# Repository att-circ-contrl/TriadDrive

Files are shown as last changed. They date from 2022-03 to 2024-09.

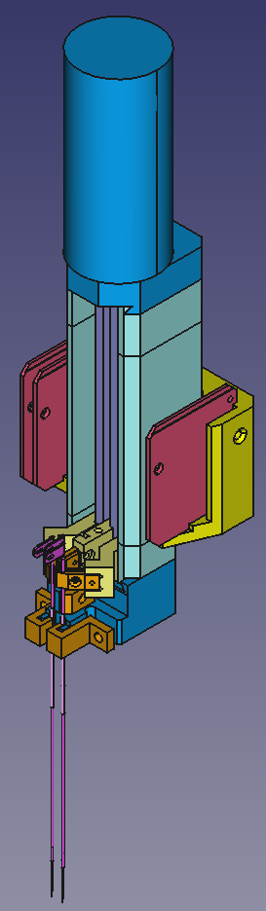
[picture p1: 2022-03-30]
drive-close-short/renders/20220329-nn-assembly-iso.png

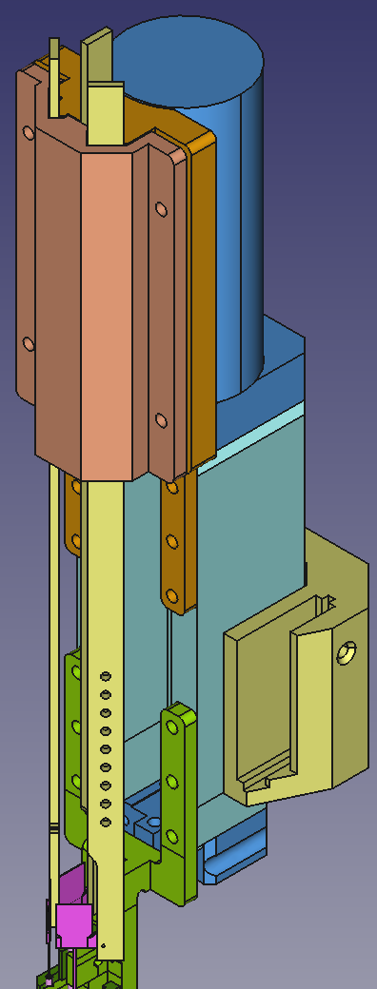
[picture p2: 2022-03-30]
drive-close-atlas/renders/20220317-rod-guide.png

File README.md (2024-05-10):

# Womelsdorf Lab Probe Drives

## Overview

This project covers the design of the probe drives used by the Womelsdorf
lab. As of 2022, these are mostly derivatives of the "Triad drive" 3-probe
drive commissioned in **FIXME - year** from Kevin Barker of Neuronitek.

The original "Triad" drive has three BNM07-1207 Namiki motors, each with a
105x reduction gear (SPG07-105). These drive #0-80 threaded rods, which move
probe-holding "arms" along paths defined by the outer shell of the drive
(the "body") and an internal "girder" with precisely-machined channels.

Derivative variants of the "Triad" drive replace the arms, the outer shell
of the drive, and the foot of the drive, but keep the basic architecture the
same and do not modify the motor section.

Alternate drive designs that are not direct derivatives of the "Triad" drive
are noted where present.

## Folders

Top-level folders:

* `aux-XXX` -- CAD files and notes specific to a given auxiliary tool.
* `drive-XXX` -- CAD files and notes specific to a given drive variant.
* `notes` -- Assorted notes that apply to several different devices.
* `obsolete` -- Devices and specifications that are no longer in service.
* `procedures` -- Assorted SOPs that apply to several different devices.
* `reference` -- Assorted reference material that isn't vendor documentation.
* `vendor-docs` -- Vendor-provided documentation and datasheets.
Under vendor copyright.

Sub-folders in `drive-XXX` and `aux-XXX`:

* `bom` -- List of vendor-supplied parts needed.
* `cad` -- Mechanical design CAD files. These are in FreeCAD format.
* `cad-ext` -- Mechanical design CAD or IGES files imported from a different
folder or provided by external sources (usually Isaac).
* `datasheets` -- Vendor-supplied mechanical drawings and component information.
* `drawings` -- Mechanical drawings of various components.
* `iges` -- Exported mechanical designs in IGES format.
* `meshes` -- Exported solid models in STL format.
* `notes` -- Assorted notes that are specific to this device.
* `photos` -- Photographs of the device or of associated equipment.
* `procedures` -- SOPs that are specific to this device.
* `renders` -- Screenshots of CAD views of various mechanical assemblies.

## Specific Designs

Active Triad drive variants are as follows:

* `drive-kevin` --
This is the initial Triad drive designed by Kevin for the Womelsdorf lab.
There were two variants: the "old" variant had a 45mm long channel for the
arms and the "new" variant had a 55mm long channel.

* `drive-close-short` -- This is a short-reach design with closely-spaced
probe sites. This drive is in service (with Kevin-style clips; the M0.5
screw-mount arms are obsolete). This can hold tungsten probes, NeuroNexus
probes, and Diagnostic BioChip probes (but not Atlas probes).

* `drive-close-long` -- This is a long-reach drive with the same
closely-spaced sites as the short-reach drive. This drive is in service.
Probes are held using Kevin-style clips. Guide tubes are held by a "foot"
that extends into the chamber. This drive is mainly used with Diagnostic
BioChip probes, which have a mechanical conflict between the probes and
guide tubes that limits range with the short-reach drives.

* `drive-close-atlas` -- This is a long-reach drive that is intended to hold
Atlas probes using the same "rectangular rod" scheme as the obsolete "v2b"
drive. This drive provides close-spaced probe sites with somewhat wider
spacing than the other close-spaced drives.

* `drive-kia-dev` -- Modified long-reach drives intended to work with
Diagnostic Bio-Chip probes, developed by one of our postdocs. This folder
contains his development tree (Autodesk CAD files, STL meshes, and gcode
for the printer he used).

Relevant auxiliary components are as follows:

* `aux-cabling` -- This folder contains documentation and models for
cables and connectors that the Triad drives and probes interface with.

* `aux-clips` -- This folder contains CAD models of clips used to hold
probes and guide tubes. Some are compatible with Kevin-style clip mounts,
while others are intended for different mounting methods.

* `aux-jig-atlas-long` -- This folder contains design files for tools for
loading Atlas probes into long-reach drives (drives that use the "rectangular
rod" system for holding probes).

* `aux-jig-nnex` -- This folder contains design files for the jig used to
pre-load NeuroNexus probes into guide tubes. The same jig works with
Diagnostic BioChip probes if the block holding the probe is shimmed with
tape to raise it.

* `aux-mounts-dbc` -- This folder contains cable mounts that replace the
mounting clip of the Triad drive. These hold the ZIF-clip connector boards
used with the 2022 Diagnostic BioChip probes.

* `aux-mounts-hflex` -- This folder contains cable mounts that replace the
mounting clip of the Triad drive. These hold the "heavy flex" analog signal
cables used with Atlas and NeuroNexus probes.

* `aux-probes` -- This folder contains CAD models of probes and CAD models
of printable components for making mechanical mock-ups of probes.

* `aux-proxies` -- This folder contains printable simplified proxy models
of drives and associated hardware. These are stencils intended to be used on
the mounting frame to check drive setups without needing to fully configure
drives.

* `aux-washers` -- This folder contains spacer "washers" used to raise the
Triad drives above their default mounting locations.

Drives not directly tied to the Triad Drive design:

* `drive-compact` -- This is a single-probe miniature manual drive intended
to be arrayed inside the chamber. This is a more manufacturable variant of
the 2018 "semi-chronic" drive concept.

* `drive-unidrive` -- This is a proof-of-concept single-probe drive based
on the same principles as the Triad drive but designed to be easier to
manufacture.

## Remarks

* I've been repeatedly reassured that the Womelsdorf Lab owns all of the IP
for the original drives that we commissioned, so there should be no IP issues
with derived variants.

* Kevin is a superb engineer. Every aspect of his original design is there
for a reason, and the reasons are not always obvious. Kevin also gets
precision about twice as good as standard "shop" precision (better than
0.1mm, vs typical shop precision of 0.15 mm or worse). The downside to this
is that understanding the original design was nontrivial and third-party
parts typically have wobble due to worse tolerances.

* I have a love/hate relationship with the `FreeCAD` program. It works
_just_ well enough that it isn't worth my time to learn a new program, but
it has strange ideas about how many operations should be done and it
lacks several features that would be helpful for building and testing
models. If you need to modify existing mechanical models, I suggest
importing `.iges` models into your preferred CAD program.

* IGES models should be saved as solids (type 186), rather than as surfaces
(type 144). Surfaces are the default, but solids can have additional
operations performed on them after import (especially boolean operations).

_This is the end of the file._

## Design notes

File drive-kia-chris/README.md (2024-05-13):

# Chris's Copy of Kia's Long-Reach Drive

## Overview

The close-spaced long-reach drive was modified by one of our postdocs
(Kia) to work more effectively with his setup. This is my annotated copy
of the parts that were put into service.

NOTE - In the future I may CAD up my own versions of these, optionally with
modifications. For now, it's just a handy way of determining which parts
were actually used out of the many variants in Kia's dev tree.

Salient changes that Kia made:

* Drive components were mostly compatible with filament-printing (he used
that for prototyping).

* Drive feet were modified to be as flat as possible, for optimum access
to sites near the side of the chamber.

* Kia used captive nuts and epoxied-in-place nuts in lieu of hand-threading
holes. This solved the durability problem with holes that were threaded in
plastic.

## Notes

Unsorted notes:

* The mockup shows the drive foot reaching into the chamber, but the other
way of using these is to use stand-offs on the mounting post to raise the
drive so that the drive foot is above the chamber. This gives access to
sites next to the chamber wall without having to have the drive reach across
the entire chamber. The mounting frame photograph illustrates this
configuration.

* There are many incremental variants of the STL files. The best way to tell
which ones are the final ones is to look at the datestamps (in the
`zz-datestamps` folder in the `drive-kia-dev` folder).

* Kia's STL files and my IGES files all have varying coordinates between
parts. I've arranged everything in the mockup and re-exported it to the
`exported` folder to try to get everything into a consistent coordinate
frame.

_This is the end of the file._

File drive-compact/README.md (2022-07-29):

# Miniature Single-Probe Drive

## Overview

This is a proof-of-concept design for a manual drive that uses the same
principles as the 2018 "semi-chronic" paperclip-sized drive, but with parts
that are easier to make and to assemble.

These are driven using a hex-drive screw that's coupled to the drive rod.
The intention is that a motorized hex driver could be placed above the drive
to allow computer-controlled driving. Hex-drive is also far less slip-prone
than flat-bladed driving for manual drive, and doesn't require pressure like
Phillips does.

## Notes

* Natural widths from assembly screw lengths are 2.4mm (3/32"), 3.2mm (1/8"),
and 4.8mm (3/16").

* Another width constraint is side wall thickness for the drive screw and
alignment pins. The drive screws are 1.5mm wide (#0-80) and the bushing tubes
around the alignment pins are 2.1mm (14ga) or 2.4mm (13ga) wide, for 1/16"
pins.

* Minimum collar width is 4mm, with D-profile shafts and 1/16" set screws.
For anything narrower, the drive shaft and drive screw will have to be
brazed or welded together inside a coupling tube.

* Natural height of the alignment pin holding frame is 1/4" (6.35mm).
Useful minimum is 5mm. Natural depth of the bottom is about 15mm (much more
and it starts conflicting with tissue, depending on location).

* Drive rod length is 1", 1-1/2", or 2", from McMaster-Carr.

* Drive screw length for socket-head is 1/2" if 316, or up to 1-1/2" 18-8.

_This is the end of the file._

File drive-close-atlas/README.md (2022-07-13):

# Close-Spaced Drive for Atlas Probes

## Overview

This folder contains a variant of the long-reach "v2b" drive that has
close-spaced sites. This drive is intended for use with flanged Atlas probes.

The probes are mounted on rectangular "rods" that are in turn moved by
modified arms. A guide block keeps the "rods" in alignment. A "fork" extends
down into the chamber, and guide tubes are mounted to the fork. The body and
rods are identical to the "v2b" version. The guide block, arms, and fork are
new.

**NOTE** - The "Atlas" drive uses the "Atlas" sites in the site diagram
(2.0mm spacing), which differs from the more closely spaced sites used with
DBC and NeuroNexus probes (1.0mm/1.5mm spacing). Distance from the mounting
post also differs.

A variant of this drive uses clip-based arms instead of rods, omitting the
rods and upper guide block. This is intended to work with tungsten probes
using the same guide tube pattern as Atlas probes.

## Atlas Notes

* The Atlas probe cables have to bend around backwards to reach the cable
mount. This is because the original Atlas use-case had heavy flex and the
drive on opposite sides of the chamber, whereas the Triad drives have
heavy flex mounted on the drives.

* Mounting the Atlas probes is non-trivial, because they break if you look
at them funny and the thin-flex connected to them isn't much stronger.

* With a plastic foot, *the side guide tube mounts deflect*, pinching off
the middle channel and moving each guide tube inwards by about 0.4mm. The
probe mounts have enough compliance to tolerate this, but it's very much
not an ideal situation.

## Clearance and 3D Printing Notes

* Arms need to be made with tolerances better than standard shop and
printing tolerances. Otherwise the clearances needed for reliable assembly
are large enough that the arms wobble. We can't actually get arms made
with the required precision, so instead several versions of the arms are
made with nominal thicknesses varying in steps of 0.05 mm. In any given
batch, one version of any given arm should be the right thickness.

* Arms with tight clearances should be oriented with their long axes in the
Z direction for 3d printing. This gives 0.05 mm tolerances on the other axes
when using Proto Labs' "micro-resolution" printing process.

* As of June 2022, the "thick" variants of the arms work best in the drives.

_This is the end of the file._

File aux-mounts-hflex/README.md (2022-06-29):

# Cable Mounts for Heavy Flex

## Overview

These folders contain models and drawings of cable mounts intended to hold
the "card" ends of the "heavy flex" cables, securing the ends of the cables
to the Triad drives.

The cable mounts replace the mounting clip on the Triad drive (holding the
drive to its mounting post).

## Notes

* The single-slot sides anchor the heavy flex cables using a 5/16" #0-80
flat-head screw. The two-slot sides use a 3/8" #0-80 flat-head screw.

* Be careful installing the screws. There's only about 2mm of threaded
area, and it's easily stripped.

_This is the end of the file._

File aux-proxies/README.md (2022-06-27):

# Mechanical Proxies

## Overview

This folder contains models of mechanical proxies of each of the drive
variants in service. These are used for planning the configuration of the
drives; proxies are mounted on a mockup chamber and adjusted to have guide
tubes in the desired locations.

(The original proxy for the stock tungsten drives was made by Brainsight
in the 2010s, I think. The new proxies are intended to be 3d printed.)

The proxies have optional obstruction templates that may be attached. Without
the templates, the goal is to show where the guide tubes will be positioned
with maximum visibility. With the templates, the goal is to see whether nearby
drives will conflict with each other.

## Specific Models

Drive proxies (representing the drive bodies and guide tubes):

* `drive-close-atlas` -- This represents the close-spaced drive for Atlas
probes with guide tube mounts inside the chamber, using the 2.0/2.0/1.5 mm
hole pattern.

* `drive-close-long` -- This represents the "close-spaced long-reach"
drive for NN and DBC probes with guide tube mounts inside the chamber, using
the 1.0/1.5/1.5 mm hole pattern.

* `drive-close-short` -- This represents the "close-spaced short-reach"
drive with guide tube mounts above the chamber, using the 1.0/1.5/1.5 mm
hole pattern.

* `drive-stock` -- This represents the stock "kevin" drive with a bundle
of three guide tubes in contact with each other.

Cable mount proxies (representing mounts for either the "heavy flex"
cables or the Diagnostic BioChip adapter boards):

* `dbc-zif-narrow` -- This represents a Diagnostic BioChip board mount plus
attached ZIF-clips, intended for narrow-body (stock) drives.

* `hflex-narrow` -- This represents a "heavy flex" mount intended for
narrow-body (stock) drives.

* `hflex-wide` -- This represents a "heavy flex" mount intended for
wide-body (Atlas) drives.

Obstruction templates (representing space taken up by drive arms and by
guide tube mounts):

* `close-atlas` -- This represents a standard (two-level) foot used with
the Atlas probe long-reach drives.

* `close-short-1pc` -- This represents a low-profile foot for the
"close-spaced short-reach" drive that uses a single clip to hold all three
guide tubes.

* `close-short-2lv` -- This represents a standard (two-level) foot for the
"close-spaced short-reach" drive that uses one clip for each guide tube.
This is also used for the "close-spaced long-reach" drive.

* `close-short-3pc` -- This represents a low-profile foot for the
"close-spaced short-reach" drive that uses one clip for each guide tube.

_This is the end of the file._

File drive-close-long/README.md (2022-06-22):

# Close-Spaced Long-Reach Drive

## Overview

This folder contains a long-reach variant of the close-spaced short-reach
drive, intended for use with Diagnostic BioChip probes. This eliminates
mechanical conflicts between the probe and guide tube, allowing the full
range of drive travel to be used (so that the probes can reach as far as
possible into tissue).

For this variant, the drive "foot" is extended to incorporate a
downward-projecting shaft similar to that of the "forks" used in
"v2b"-derived drives. This results in geometry that is difficult to machine,
but 3d printed versions should work (the shaft is 3mm thick to ensure
sufficient strength and rigidity).

Guide tubes are in the same locations as with the close-spaced short-reach
drives, so the stock (narrow) body and short-reach drive's arms are used.

## Clearance and 3D Printing Notes

* Arms need to be made with tolerances better than standard shop and
printing tolerances. Otherwise the clearances needed for reliable assembly
are large enough that the arms wobble. We can't actually get arms made
with the required precision, so instead several versions of the arms are
made with nominal thicknesses varying in steps of 0.05 mm. In any given
batch, one version of any given arm should be the right thickness.

* Arms with tight clearances should be oriented with their long axes in the
Z direction for 3d printing. This gives 0.05 mm tolerances on the other axes
when using Proto Labs' "micro-resolution" printing process.

* As of June 2022, the "wide" variants of the arms work best in the drives.

_This is the end of the file._

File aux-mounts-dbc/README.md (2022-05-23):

# Board Mounts for Diagnostic BioChips Probes

## Overview

These folders contain models and drawings of board mounts intended to hold
the boards and ZIF-clips used with Diagnostic BioChips probes. The boards
screw into the mounts and the ZIF-clips clip on to the boards.

The board mounts replace the mounting clip on the Triad drive (holding the
drive to its mounting post).

## Notes

* These are intended to be 3d printed in a rigid plastic. Nylon and printed
polypropylene flex too much at the mounting posts.

* The new versions of these mounts attach Kevin-style. The two faces on
each side of the post aren't flush with each other. One mates with the
drive, leaving a small amount of clearance in the post channel. The the
other has clearance, allowing the clamp to bend as the screw is tightened
until the post and channel fully engage with each other.

* There are multiple versions of the mounts, with different post channel
widths. Choose the version that has the least clearance around the post.
Different versions are identified by different markings.

_This is the end of the file._

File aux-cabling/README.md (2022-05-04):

# Cables and Connectors

## Overview

This folder contains drawings and models for some of the cables and
connectors used with the Triad drives and probes.

This is not a complete list or a complete specification; those are beyond
the scope of this project. The intent is to provide enough information to
allow compatible cable mounts and cabling arrangements to be designed.

## Specific Cables and Connectors

* We use custom headstages built into 128-channel TDT ZIF-clips. A rough
model of a ZC128 clip is provided.

* The "heavy flex" cables are used to connect Atlas and NeuroNexus probes to
ZIF clips (and to provide strain relief). In both cases, the probe is
connected to the heavy flex via a much smaller "thin flex" cable.

## CAD Files

* The "`atlas-flex-2020.fcstd`" CAD file contains a model of the thin-flex
Atlas cable, and an assembly of these cables with the "carrier card" from
the heavy-flex cable. The "carrier card" model is reconstructed from a mesh,
rather than from the original solid model.

_This is the end of the file._

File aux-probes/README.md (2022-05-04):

# Probe Models

## Overview

This folder contains drawings and models for the probes used with the
Triad drives.

This is not a complete specification; that's beyond the scope of this
project. The intent is to provide enough information to allow the design of
drives that are mechanically compatible with the probes.

## Specific Probes

* Atlas probes were ordered in 2017.

These were originally intended to be used with a dense-packed semi-chronic
drive, which secured the probes and guide tubes to the drive with flanges
and tiny screws. With the Triad drive we can use different guide tubes and
clamp them normally, but the probes will have to be secured with screws (the
flanges are permanently bonded and the probe shanks are too fragile to
reliably grab).

The Atlas probes have "thin flex" ribbons that connect to our "heavy flex"
cables. The Atlas probes are permanently bonded to the heavy flex.

* NeuroNexus probes were ordered in 2018 and 2021.

They were ordered with flanges for compatibility with the Atlas drive
hardware, but in practice are secured using clips. The shanks are stainless
steel tubes, making them much easier to secure and to handle.

The NeuroNexus probes have hair-thin flex cables which are bonded to tabs
that connect to our "heavy flex" cables. These may be connected and
disconnected from the heavy flex as-desired.

* Diagnostic BioChip probes were ordered in 2022.

These do not have flanges, but instead have a 5mm collar of hypodermic
tubing for handling.

The DBC probes do not connect to "heavy flex". Instead, they have their own
ZIF-clip compatible adapter cards, which are connected to the probes using
a short length of delicate thin flex. The adapter cards need to be mounted
close to the probes and the ZIF-clips need to connect directly to the adapter
cards.

## CAD File Notes

* The presently active CAD file is "`probe-models-2022.fcstd`".

* The 2020 CAD file contains old models for NeuroNexus probes. The "sleeve"
version was an alternate implementation that wasn't made; it can be ignored.
The file has copies of the old Atlas models, but these were reconstructed
from meshes instead of from the original solid models.

_This is the end of the file._

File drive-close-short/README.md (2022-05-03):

# Close-Spaced Short-Reach Drive

## Overview

This is a modification of the "stock" Triad drive that replaces the foot
and the arms (in the same manner as the "v2c" variant did). It keeps the
original "narrow" body.

"Silicon" arms with holes to screw in flanged probes were made, but were a
pain to use, and it turned out that NeuroNexus probes can be held by the
clips Kevin provided to us (albeit at risk of metal fatigue). So, only the
"tungsten" arms are needed with this design.

This design can work with tungsten, NeuroNexus, and Diagnostic BioChip
probes, with appropriate cable holders.

## Variants

The following variants are in service:

* The "stacked" foot is the original version, with the middle guide tube
clip raised above the side clips. The central guide tube is held with a
flat "6p5" clip and the side guide tubes are held with "J-clip" clips.

* The "1pc" low-profile foot uses a single clamp to hold all three guide
tubes. It's difficult to individually adjust guide tubes with this drive,
and removing any guide tube requires removing the clamp.

* The "3pc" low-profile foot uses three clamps to hold the guide tubes, with
the middle clamp screwing into the side clamps rather than into the base of
the drive. In principle the guide tubes can be individually adjusted with
this setup (though adjusting any screw alters pressure on all three clamps).
Removing either of the side guide tubes requires first removing the middle
clamp.

## Notes

* The IGES files for the foot and J-clip are surfaces, not solids.
* I think Isaac's exported arms are solids but I'm not certain.
* The original version (from 2021-11-04, with Z-clips) didn't work; the
clips would slide off of the guide tubes. The J-clips fixed this (from
2021-11-18).
* The "`triad-arms-ref-202203`" CAD file imported Isaac's arms for purposes
of making mechanical drawings. These are not authoritative but are a good
starting point. The DBC arms are the current version.
* FIXME - As of 2022-04-21, I'm not sure either the 1pc or 3pc clamps will
work (untested). The 1pc one might have difficulty grabbing the middle tube
due to bowing, and the 3pc one may have difficulty grabbing the side tubes
when the middle clamp is tightened and/or difficulty installing the middle
clamp when the side clamps are tightened.

_This is the end of the file._

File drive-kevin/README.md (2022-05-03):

# Stock ("Kevin") Triad Drive

## Overview

This folder documents the "stock" version of the Triad drive. These were
produced by Kevin Barker of Neuronitek on a contract for Thilo's lab.

## Notes

* Most parts were made by machining, but some parts were made by EDM by a
third-party vendor (I'm not sure who Kevin used for this).

* Kevin miniaturized the drives as much as possible (at Thilo's request).
Consequences of this include additional complexity, thin walls near several
holes, and the need for extremely close tolerances.

* Kevin got part fits with tolerances about twice as good as any other
vendor I'm aware of (about 0.05 mm as far as I can tell). He did this by
a combination fo careful setup and by hand-modifying individual sets of
mating parts.

The practical upshot of this is that any parts we get made for the Triad
drives will be a bit loose, due to the fact that we can't precisely match
the fit with the existing parts.

* The models in the "`iges`" folder should be considered authoritative.
These are my best guess as to the geometry of the actual parts. NOTE - These
were exported as surfaces rather than solids, so there may be issues
importing them.

* There are two types of meshes in the "`stl`" folder. Ones with the "`-sw`"
suffix have been modified to be compatible with Shapeways' 3d printing
design rules (mostly avoiding sharp concave edges and thin walls). Ones
without the "`-sw`" suffix were exported from the original models as-is.

## Variants

* The "old" variants have 45mm bodies made from black Delrin. The "new"
variants have 55mm bodies made from white Delrin. The "new" variants are
labelled "rev 3".

* The guide tube clip geometry is different for "old" and "new" variants.
The foot's mounting for the guide tube clip is also different.

* At least one variant exists that mounts five or six probes and guide
tubes (two per arm). If I understand correctly these were used for SPME
experiments.

_This is the end of the file._

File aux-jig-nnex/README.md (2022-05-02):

# Hand-Loading Jig for NeuroNexus Probes

## Overview

This folder contains drawings and models for a jig used to load NeuroNexus
probes into guide tubes.

**NOTE** - This is presently also used to load Diagnostic BioChip probes
into guide tubes, but the probe holding part needs to be shimmed on the
bottom with masking tape in order to have the correct alignment.

## Using the Jig

To use the jig:
* Clamp the guide tube on to the right (moving) block. Move it a safe
distance away.
* Place the probe on the left (fixed) block. The green tab on the NeuroNexus
probes can be placed to stand up in one of the grooves in the rubber
portion; for DBC probes, just rest the card on the rubber.
* Holding the probe in place with a fingertip, clamp it down.
* Put the surgical loupe on. You're going to have to align the probe tip and
guide tube by eye.
* Move the guide tube closer to the probe. When the probe tip and the
entrance to the guide tube are near each other, ensure that they are aligned
by applying gentle pressure to the mounting blocks (they can deform slightly),
and/or by applying gentle pressure to the clamp holding the probe (the probe
will bow slightly, adjusting its height).
* When the probe and guide tube are aligned, bring them together.
* When the probe is fully inserted, hold the probe and guide tube in place
with a fingertip and un-clamp both.
* Remove the probe and guide tube by holding the guide tube with forceps,
keeping it tilted up so that gravity moves the probe into the tube instead
of out of the tube. Hold the green tab (NN) or circuit board (DBC) with
forceps to prevent it from pulling on the thin flex.

## Miscellaneous Notes

* Some or all of the IGES models will have been exported as surfaces rather
than solids.

_This is the end of the file._

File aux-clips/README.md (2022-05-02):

# Clips for Probes and Guide Tubes

## Overview

This folder contains drawings and models for some of the clips used to hold
probes and to hold guide tubes with the Triad drives.

This is not a complete list, but should cover the types that are presently
in service. Historically two other attachment methods were also used (using
screws and flanges to mount individual probes and guide tubes, and using
a larger clamp to hold multiple guide tubes at once), but clips were the
most practical system.

The guiding principles are as follows:

* It should be possible to remove individual probes and guide tubes without
disturbing the others.

* It should be possible to position probe sites close to each other (2mm or
closer).

* Nobody should have to reinstall M1 screws or do anything with M0.5
screws in order to add or remove probes or guide tubes. #0 screws are
preferred over M1 where practical.

Several fabrication methods are available:

* 3D printing was used for large clamps and is still used for the assemblies
that clips screw on to. Printed plastic parts are too weak to use for the
clips themselves and printed metal parts have resolution too poor to use,
with rare exceptions.

* CNC machining is used where practical, but has strong constraints on
geometry (in particular thickness).

* EDM is used for making thin clips with high precision out of stainless
steel, but finding vendors for this is a pain and turnaround time is long.

## Specific Clips

* The "Kevin" clips were made by EDM and were intended to hold 200 micron
tungsten probes. In practice they'll hold 125 micron probes that are
shimmed with tape, and they've been used to hold 400 micron NeuroNexus
probes (although this will eventually cause metal fatigue). These use M1
screws for mounting and for closing.

* The "6p5" straight clips are made out of CNC machined PEEK. These use #0
screws for mounting and closing and are somewhat bulkier than Kevin clips.

* The "j-clip" clips are made from 3d printed resin (Proto Labs' "ABS-like
micro-resolution" process). These are used as guide tube clamps with
certain close-spaced probe layouts. The geometry and tolerances made 3d
printing the only option. So far they've held up in use.

* The "compat-630" EDM clips are very similar to the Kevin clips and are
intended to hold 630 micron guide tubes and probe collars.

* The "cnc-630" clips were intended to hold 630 micron guide tubes and
probe collars and to be made using Proto Labs' CNC service.
**Obsolete** - They ended up being too bulky and Proto Labs wouldn't
machine the probe registration notches.

* The "3dp-630" clips were intended to hold 630 micron guide tubes and
probe collars and to be made using Proto Labs' stainless steel 3d printing
service. **NOTE** - These are very difficult to hand-tap.

_This is the end of the file._

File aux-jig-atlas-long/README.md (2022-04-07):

# Atlas Probe-Loading Tools for Long-Reach Drives

## Overview

This is a jig and a set of manipulation tools intended for attaching Atlas
probes to the "rectangular rods" used by long-reach drives, and for mounting
the probe-and-rod units into those drives.

## Notes

* The probe needs to be held by its flange, using a padded clamp. If the
flex cable is held instead, the probe bounces around and is very difficult
to control. Attempting to hold the shank will break the probe (they break if
you look at them funny).

* After the two parts are attached, the clamp has to hold the probe to the
rod semi-rigidly to prevent forces on the cable from moving the probe, but
needs to have enough compliance to allow the probe tip to be manually aimed
at the guide tube.

* As with any Atlas probe setup, the M0.5 screw holding the probe needs to
be backed off half a turn so that the probe can move enough to self-align
with the guide tube.

_This is the end of the file._

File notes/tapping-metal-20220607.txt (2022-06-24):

Notes for tapping M1 threads in 3d printed steel clips:

- As soon as there's _any_ resistance (about half a turn of cutting), back
  off half a turn to a full turn.
- If there's still resistance when resuming after that, back all the way
  out and clear chps with canned air.

This was for relatively shallow holes (1mm deep).

This should work for brass, aluminum, and 3d printed 316 steel. It may not
work with hard steel (heat-treated printed 17PH, machined steel parts, etc).

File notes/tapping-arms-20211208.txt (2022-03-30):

To tap 3d printed plastic arms without damage:

- Use the 3/64" (#0 tap) drill to widen the holes.
- Start tapping. As soon as there's resistance, _stop_ and back out.
- Use canned air to clean the tap and clear the hole.
- Resume tapping. As soon as there's resistance, _stop_ and back out.
- Repeat the above steps until the hole is fully tapped.
- Clean the tap and clear the hole, and then run the tap through the hole
  again for a finishing pass.
- Clean the tap and clear the hole, and use a #0-80 screw to test the hole.
  The screw should engage easily with no resistance at any point.

Tapping too aggressively does the following:

- The side-walls bulge out. Best-case they'll need to be filed down, and
  in the worst case they'll break (prints are weak and walls are thin).
- The side-walls will apply pressure, squeezing the screw. This will cause
  the arm to get stuck on the drive screw.

.. The procedure outlined above will eliminate these problems.

It's a good idea to use a similar procedure with harder materials, too. It's
also important to back out and break chips when working with, e.g., PEEK.

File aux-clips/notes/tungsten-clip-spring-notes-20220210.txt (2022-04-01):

Microscope measurements gave:

- Spring is 0.25 mm thick.
- Clearance between flats was 0.05 mm.

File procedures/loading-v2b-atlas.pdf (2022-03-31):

Loading Atlas Probes Into the v2b Triad Drives Christopher Thomas - 2020 July 17

FIXME - Add photos

1. Remove the cable shelf assembly and Triad mounting post from the “first and second probe” base plate.
2. Insert the Triad drive on to the mounting post, install the mounting post on to the base plate, and then reinstall the cable shelf assembly on the base plate.
3. Move the Triad arms to their topmost positions.
4. Install the “first” cannula jig, using shims to adjust the height. Verify positioning with a loupe.
5. Install the “first” probe jig. The probe jig should start flush-right in its well, to give it space to move left. Install the thin flex clip screw, but not the clip itself, in the probe jig.
6. Move the middle Triad arm down to register with the probe jig. Verify that the arm is seated on the jig shelf. Adjust this by changing shims.
7. Open the heavy flex clip. Holding the probe assembly’s thin flex using forceps and the heavy flex using your hand, position the probe near its loading position. Keep the probe above and slightly away from the Triad drive so that no probe contact occurs. Close the heavy flex clip to secure the heavy flex.
8. Transfer the forceps to your dominant hand, and place the probe across the probe jig with its tip over the cannula jig, adjusting it to its loading position. Install the thin flex clip by placing it, pressing down on it by hand, and tightening its screw with your other hand.
9. Visually inspect the probe shuttle using the loupe, verifying that it overlaps the mounting hole. Make small adjustments to the shuttle’s position if necessary by slightly loosening the thin flex retaining clip and moving the thin flex gently.
10. Rotate the entire mounting assembly so that you can see the shuttle and its mounting hole and easily access both of these with fine-point forceps.
11. Hold a M0.5 screw in the forceps with your non-dominant hand. Position its tip in the mounting hole and turn it two full turns using a miniature screwdriver in your dominant hand. The idea is to have it engage with the threads so that you can let go with the forceps.
12. Use your fingertips or fingernails on your non-dominant hand to stabilize the screwdriver tip while fully driving the screw. After reaching the screw’s limiting position, back it off by half a turn to allow the probe shuttle to slide and pivot.
13. Undo and remove the thin flex retaining clip. Also remove the screw that held the retaining clip.
14. Pressing the probe mounting jig towards the Triad drive, remove the mounting jig screw. Remove the probe jig shims, allowing the jig to drop while continuing to press it towards the drive (so that it does not contact any part of the probe). When the jig has dropped, remove it.

15. Align the probe with the registration surfaces on the cannula jig by applying gentle pressure to the thin flex, shuttle, and if necessary upper part of the probe shank. Use the loupe to verify that the probe is registered with the cannula.
16. Advance the probe tip into the cannula. Hand-feed the heavy flex cable through the (closed) heavy flex clip as necessary during this process. The desired stopping point is before the thin flex of the middle probe would interfere with loading the next probe.
17. Press the cannula jig towards the Triad drive, and remove it in the same manner as with the previous jig.
18. Seat the “second” cannula jig and “second” probe jig in the same manner as the first, with the second cannula jig aligned with the cannula and the second probe jig flush right..
19. Advance the upper arm of the Triad drive until it contacts the second probe jig. This arm should be to the left of the first probe’s thin flex, ensuring no mechanical conflict between the two flex cables after loading.
20. Position the second probe in its probe jig in the same manner as with the first probe (holding it by the thin flex near the probe, securing the heavy flex, manipulating the probe into position using the thin flex, and then securing the shuttle and thin flex). NOTE
- The position of the arms should result in the second probe’s tip being in a safe position over the cannula jig. If this is not the case, adjust the positions of the two arms until the probe may be safely positioned.
21. Install the second probe’s mounting screw in the same manner as with the first probe (rotating the jig assembly to a convenient position, holding the screw during the first two turns using forceps, advancing the screw fully, then backing off half a turn).
22. Remove the thin flex retaining clip and its screw from the probe jig.
23. Press the second probe jig towards the Triad drive, and remove it in the same manner as the first probe jig. Take care that it doesn’t apply undue force to the first probe’s thin flex when it drops (a small amount of contact can be tolerated). If necessary, remove shims one at a time to drop the jig in a controlled manner.
24. Register the second probe with the second cannula jig, using a loupe to verify that it will cleanly enter its cannula.
25. Advance the second probe into the cannula, stopping when its arm is aligned with the arm holding the first probe. Feed the second probe’s heavy flex through the (closed) heavy flex clip as necessary, taking care not to unduly perturb the first probe’s heavy flex.
26. Advance both probes into their respective cannulae, feeding both heavy flex cables as necessary. Stop when the tips of both probes become visible, and withdraw the probes 2mm past the point where the tips are no longer visible (to protect them from damage).
27. Install the heavy flex cables in their slots in the cable mount, advancing the heavy flex cables through their retaining clip as needed. When the cables have been screwed into their mount, the heavy flex clip may be opened.
28. Unscrew and remove the heavy flex clip assembly. Unscrew the Triad mounting post, and pick up the Triad drive (with mounting post). Loosen the clip mounting screws slightly, and remove the mourning post from the Triad drive.

29. Remove the heavy flex clip assembly and mounting post from the “third probe” base plate. Install the Triad drive on the mounting post, install the mounting post on the “third probe” base plate, and then install the heavy flex clip assembly on the “third probe” base plate.
30. Install the “third” cannula jig and the “third” probe jig as with previous probes. The probe jig should start off flush left.
31. Advance the last arm until it contacts the probe jig. Adjust shims for the probe jig ase in previous steps.
32. Position the third probe using the same method as with previous probes (holding it by the thin flex just above the probe, securing the heavy flex, adjusting position, and securing the shuttle and thin flex).
33. Install the third probe’s mounting screw in the same manner as with previous probes (making sure to back it off half a turn to allow movement).
34. Remove the thin flex clip and its screw from the probe jig. Press the probe jig towards the Triad drive, and remove it in the same manner as with the second probe jig (removing thin shims to drop it in a controlled manner).
35. Align the third probe with its cannula in the same manner as with previous probes. Advance it into the cannula, feeding the heavy flex through its clip as needed. The desired stopping point is at least 4mm into the cannula, so that lateral forces will cause the shank rather than the probe tip to touch the side of the cannula.
36. Press the cannula jig towards the Triad drive, and remove it in the same manner as the second cannula jig (removing thin shims to drop it in a controlled manner).
37. Advance the third probe until its tip is visible, feeding the heavy flex cable as needed. Withdraw the third probe 2mm past the point where its tip ceases to be visible.
38. Install the third probe’s heavy flex in the cable mount.
39. Un-clip the heavy flex, remove the heavy flex assembly, unscrew the Triad mounting post from the base plate, pick up the Triad drive, and remove the Triad mounting post from the Triad drive. The drive is now loaded.

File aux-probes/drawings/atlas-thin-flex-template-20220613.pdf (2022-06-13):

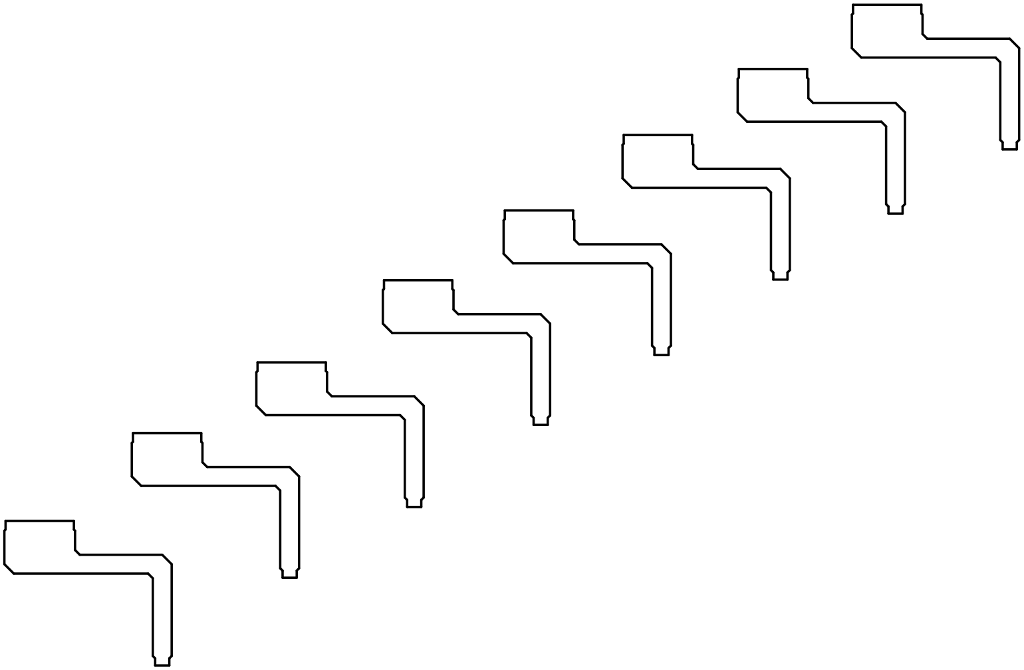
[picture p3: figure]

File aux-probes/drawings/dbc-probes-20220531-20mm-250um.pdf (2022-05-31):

# Diagnostic BioChip Probes

## 31 May 2022

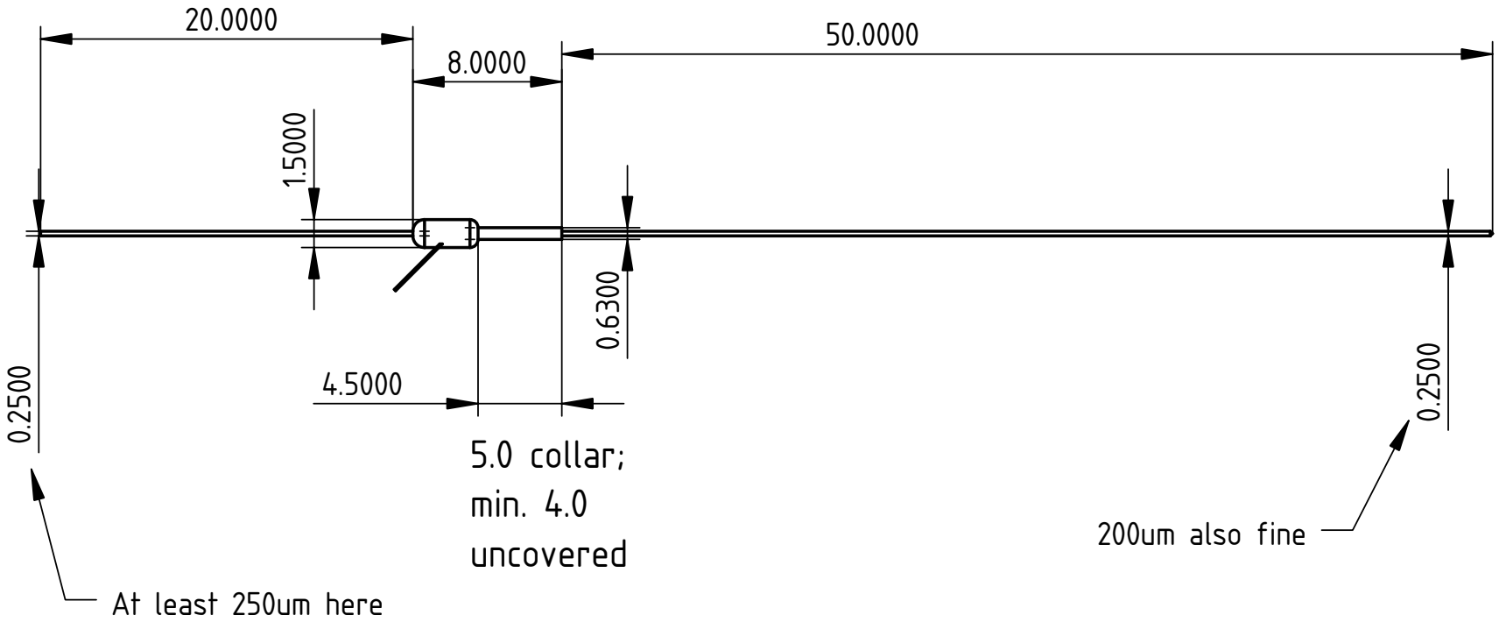
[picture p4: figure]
200um also fine; At least 250um here; 5.0 collar; min. 4.0 uncovered

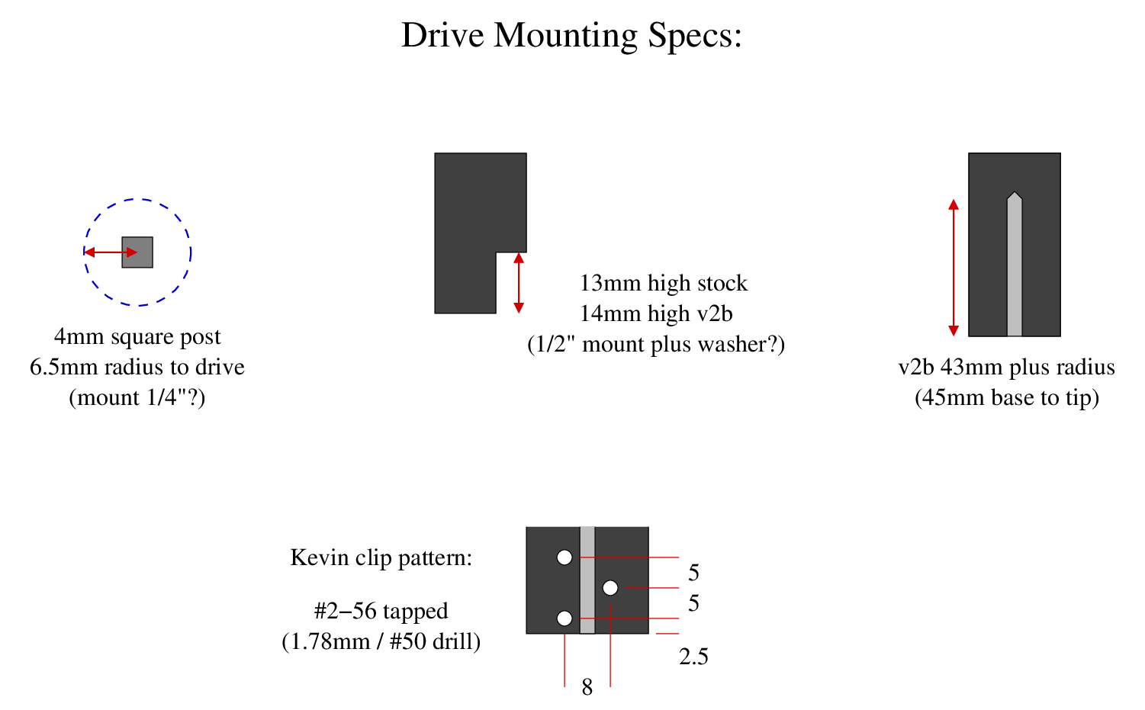
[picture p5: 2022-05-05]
notes/drive-mounting-dims/drive-base-specs.png

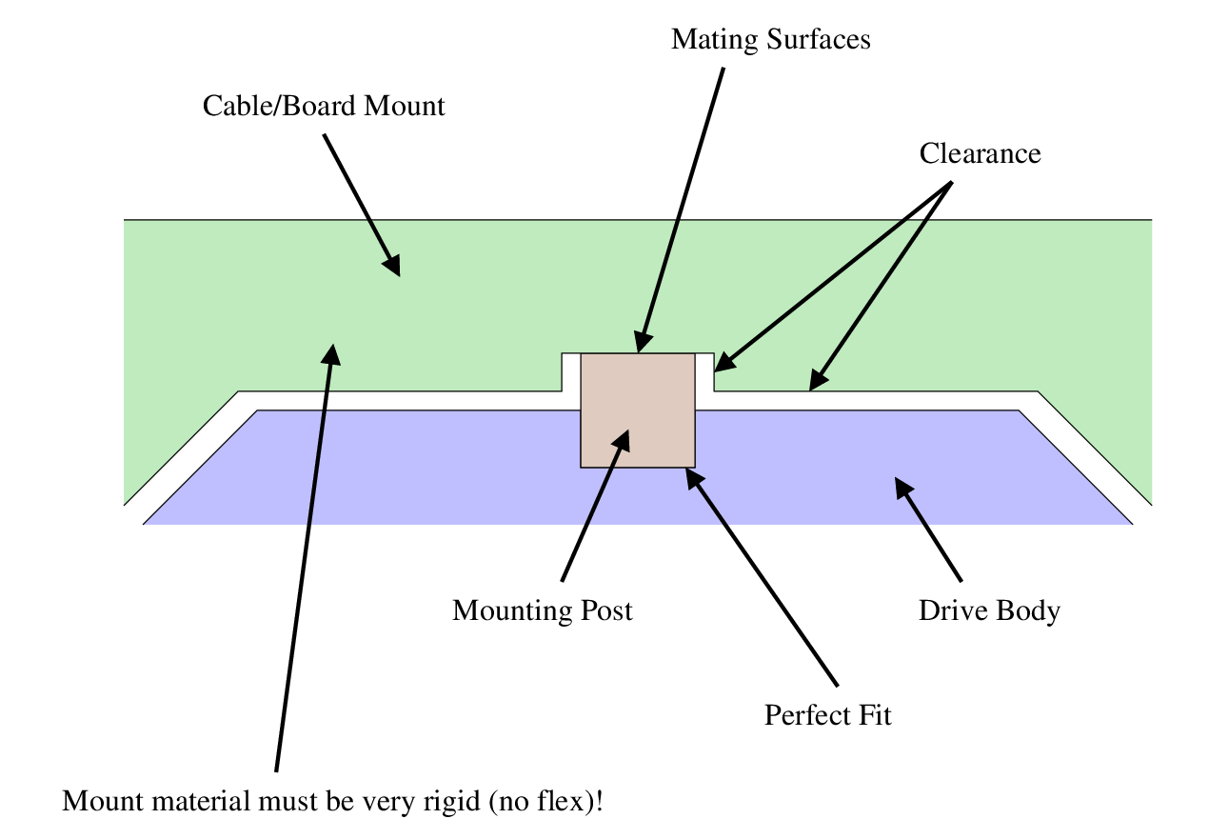
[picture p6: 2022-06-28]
notes/drive-mounting-dims/board-mount-specs.png

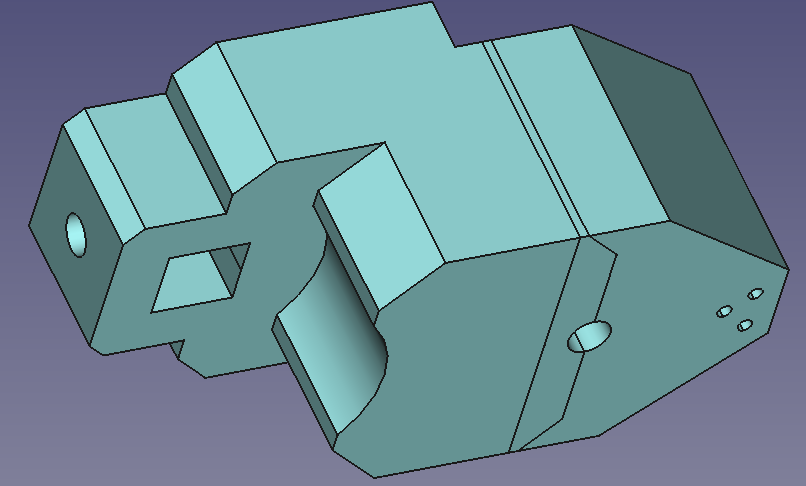
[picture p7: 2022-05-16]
aux-proxies/renders/proxy-close-short-body.png

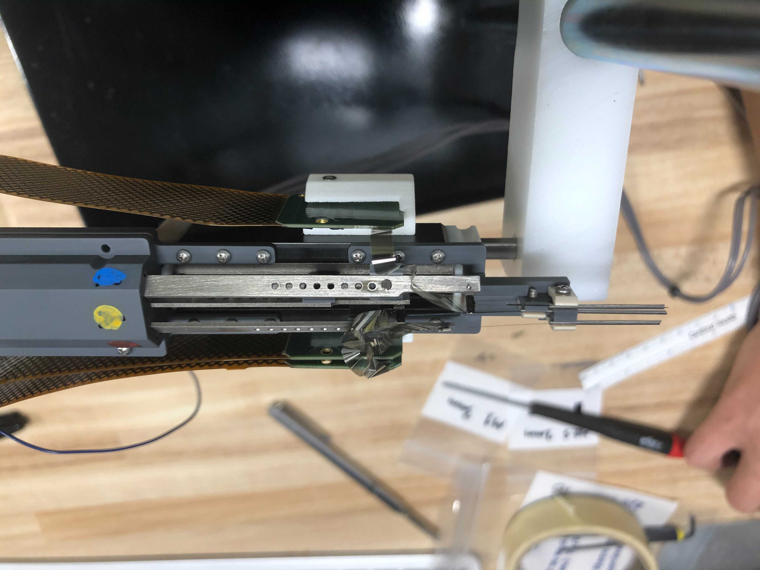
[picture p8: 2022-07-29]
drive-close-atlas/photos/orig/20220725b-atlas-loaded.jpg

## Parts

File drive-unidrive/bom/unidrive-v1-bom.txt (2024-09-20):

Parts for the v1 release candidate Unidrive:

(1x)  2" #0-80 threaded rod 316 stainless (mmc 90575A116)
(2x)  #0-80 screw 3/16" pan phillips 18-8 ss (mmc 91772A054)
(2x)  #0-80 screw 1/4" flat phillips 18-8 ss (mmc 91771A055)
(2x)  #0-80 screw 3/8" flat phillips 18-8 ss (mmc 91771A057)
(3x)  #2-65 screw 1-3/4" socket 18-8 ss (mmc 92196A947)
(2x)  #0-80 set screw 3/32" cup point 18-8 ss (mmc 92311A051)

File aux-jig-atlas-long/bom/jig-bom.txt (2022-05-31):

McMaster-Carr:

(soft pads for the tweezers)
86045K49	1/32" adhesive-backed food-grade silicone (get Shore 40A)
86045K51	1/16" adhesive-backed food-grade silicone (get Shore 40A)
86045K52	3/32" adhesive-backed food-grade silicone (get Shore 40A)

(springs for the tweezers)
1986K332	spring ss 1" len 0.188" OD 0.63 lbs/in
1986K524	spring ss 1" len 0.18" OD 2.62 lbs/in

(screws for the tweezers, the hold-downs, and the base plate)
91770A011	#4-40 truss-head 5/8" stainless steel screws (hold-downs)
91770A148	#6-32 truss-head 1/2" stainless steel screws (tweezers)
91770A150	#6-32 truss-head 5/8" stainless steel screws (base plate)

Digikey:

(clip for heavy flex)
RPC1190-ND	Manufacturer part number FCWSF-29-19.

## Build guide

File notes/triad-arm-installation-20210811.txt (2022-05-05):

[From 11 August 2021 notes.]

- Test the fit on the girder first, but also with the girder hand-seated in
  the body (for clearance with the side arms). Arms should move freely after
  initial friction. Greasing is okay.

- Drill the hole wider (to 90% #0-80 rather than 80%).
- Tap it and clear chips.
- Put a drop of oil on the hole.
- Test it with a 1/4" #0-80 screw. If there's _any_ friction at any point,
  tap it again. Repeat as necessary.

- Line up all three arms in your work area so that you know which go on which
  threaded rods. Check with the girder if unsure. The girder's flat end is at
  the bottom of the drive.

- Make sure the drive rods are free of dust.
- Put a drop of oil on the end of a drive rod.
- Tell the rod to advance upwards 10mm.
- When it starts this, hold the rod near the end to keep it from wobbling.
  Greased gloves help (they'll already be greasy, don't worry).
- Carefully orient the arm and feed it on to the rod. If it's cross-threaded,
  let go _immediately_ and hit the "stop" button. Advance down to unthread.
- This is easier if you have two people, so that one person can manually hold
  the "advance up/down" buttons instead of telling it to auto-advance.

- After feeding all three arms on to the end of the drive, add the girder and
  then reassemble the drive foot and body.
- Feed the arms back down to the bottom and set the location to 50mm.
- Feed the arms up to 5mm. Add oil to the threaded rods if they look dry at
  any point of this. Better to have too much oil than to have arms binding.
- Feed the arms back down to loading positions. They need to be staggered so
  that the screws on all of them are accessible (e.g. 35/40/45 mm).
- If the drive has enough oil to actually be dripping, blot the excess with
  paper towel. Check very carefully that no paper fibers are fouling threads.

(This is the end of the file.)

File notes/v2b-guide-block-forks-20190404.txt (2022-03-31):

Post-mortem on the v1 adapter and mount:

- Guide block trenches need to be flared at the bottom to avoid catching on
holes in the rods. Maybe flare at the top too.

- Guide block rounded cutout needs to be 2mm higher, for full range of motion
of the arms.

- _Maybe_ make arms 1mm shorter, for easier tapping? Kevin made ones this
long, though.

- Carrier arms are slightly large. This seems to be resin tolerances rather
than drawing issues, but they'll still be a very tight fit.

- Posts have trouble seating in the adapter. The posts are slightly wide
and the trench is slightly narrow. For Shapeways prototypes, adjust both.

- Post base should be slightly longer than the clamp inset/clamp inset
should be slightly deeper, so that the washer does not hold the post in
place.

- Mount arm-clamp needs to be a tighter fit around the post. Right now
there's 0.2 mm clearance, and it can't tighten enough to grip with that,
even with plastic flexing.

- Threading exit holes in the crescent need to be 1/8" farther back, for
longer threaded holes.

This is the end of the file.

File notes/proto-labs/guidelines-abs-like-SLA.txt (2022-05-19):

Design guidelines for "normal resolution" SLA ("abs-like" works well):

- max 10x10x10in (about 250x250x250 mm)
- layers 4 thou (0.10 mm)
- features 10 thou XY, 16 thou Z (0.25 mm and 0.4 mm)
- minimum wall 10 thou (0.25 mm)
- minimum hole 25 thou (0.65 mm)
- tolerances 2 thou (0.05mm) XY, 5 thou (0.13 mm) Z, plus 0.1%.

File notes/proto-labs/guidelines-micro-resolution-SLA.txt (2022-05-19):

Design guidelines for "micro-resolution" SLA:

- max 5x5x2.5in (about 120x120x60 mm)
- layers 1 thou (0.025 mm)
- features 2.5 thou XY, 8 thou Z (0.05 mm and 0.2 mm)
- minimum wall 2.5 thou (0.06 mm)
- minimum hole 15 thou (0.4 mm)
- tolerances 2 thou (0.05mm) XY, 5 thou (0.13 mm) Z, plus 0.1%.

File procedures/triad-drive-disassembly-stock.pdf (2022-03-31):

## Disassembling a Stock (Tungsten) Triad Drive

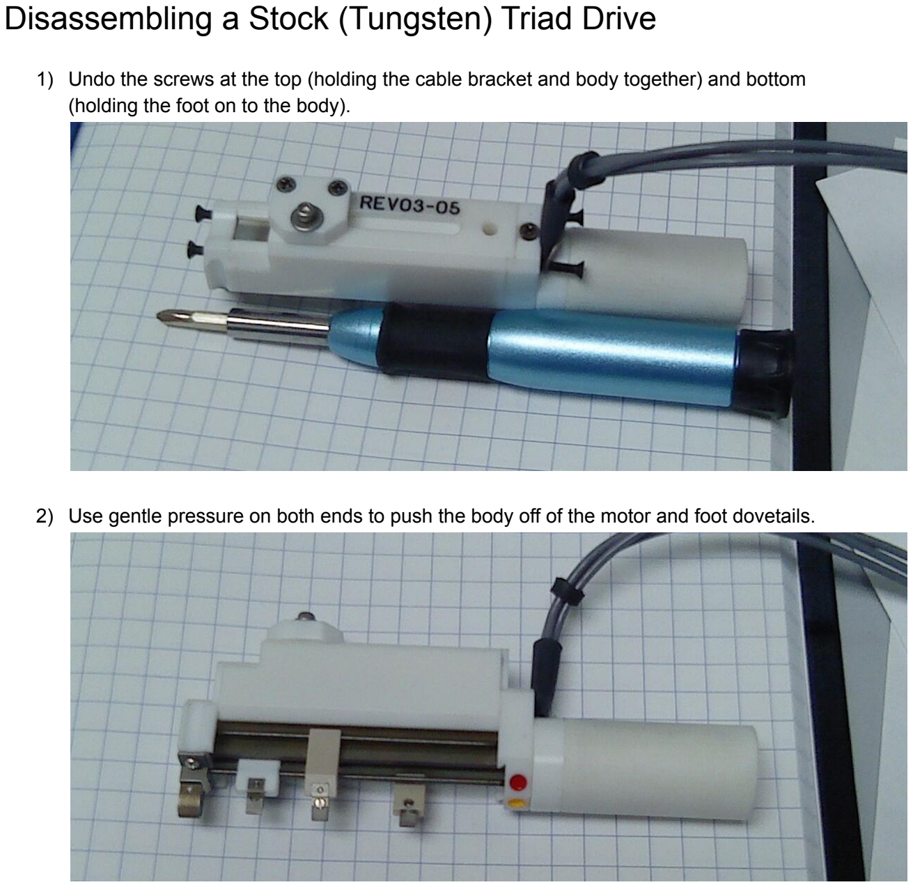
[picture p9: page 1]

1) Undo the screws at the top (holding the cable bracket and body together) and bottom (holding the foot on to the body).
2) Use gentle pressure on both ends to push the body off of the motor and foot dovetails.

3) Remove the foot, keeping the girder in place.

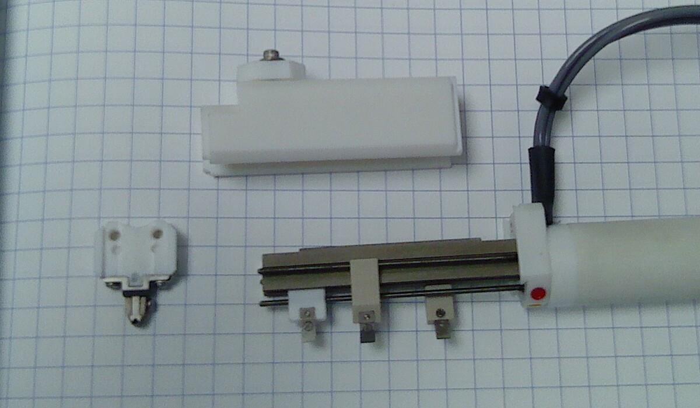
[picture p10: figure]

4) Reinstall the body without the foot present (this helps keep the arms on the girder).
5) Advance the arms off the ends of their threaded rods.

For reassembly:

- Check the threaded rod threads for fouling before reassembly.
- Apply a small amount of silicone oil to the threaded holes in the arms and to the threaded rods as-needed.
- When reinstalling the body, make sure the body is snug against the girder (i.e. that the girder is all the way back against the body). Otherwise the arms can jam.

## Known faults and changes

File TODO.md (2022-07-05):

# Womelsdorf Lab probe drives bug list, feature requests, and abbreviated changelog.

## Near-term to-do list:

* Make a model of the Kevin drive's tungsten clips. (done? check this)

* Make printable versions of the long-reach Atlas silicon arms with tighter
clearances. (r2 done; need r3 with closer trenches)

* Make a detailed explanation of how to compute bending strain, per my
notes from 23 May 2022 p2. Or just scan that page.

* Fix broken object body links for close short arms and close long atlas
arms. They should point to the version before the marker, to not be sensitive
to the number of marker dots. (done? check this)

* For the close-spaced Atlas drive's guide, shorten the lid's middle pedestal
so that the side rods can be snug when it's tightened. Also narrow the middle
trench slightly.

## Long-term to-do list:

* Consider removing this document, since it's not kept up-to-date.

## Abbreviated changelog:

* 30 June 2022 --
Release milestone with all drives and accessories at least nominally working.

* 5 May 2022 --
Release milestone with all relevant files from my old dev tree moved to the
repository.

* 4 May 2022 --
Milestone with my old "cad" folder emptied out. Still need to deal with the
"specs" folder, and consider porting more old "from isaac" material.

* 30 Mar 2022 --
Rearranged project files into something resembling a sensible tree. Created
initial repository.

_This is the end of the file._

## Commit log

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2022-03-30 Added unidrive drive.
    [gearmotor-bmn07-12-spg07-105.iges, gearmotor-proxy.stl, proxy-guide-tube.iges, proxy-nnex-probe.iges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]
2022-03-30 Moved unidrive CAD files to correct location.
    [unidrive.fcstd]
2022-03-30 Added close-spaced short-reach drive.
    [2021-triad-short-close-arm-left-tungsten.iges, 2021-triad-short-close-arm-middle-tungsten.iges, 2021-triad-short-close-arm-right-tungsten.iges, 2021-triad-shor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]
2022-03-30 Added DBC configuration of the short drive. Added assembly meshes for NN and DBC short drives.
    [20220322-dbc-model-drive-empty.stl, 20220322-dbc-model-drive-loaded.stl, 20220322-dbc-model-guide-tubes.stl, 20220322-dbc-model-probes.stl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]
2022-03-30 Added long-reach close-spaced drives. Tweaked README files.
    [2022-atlas-arm-1b-left.iges, 2022-atlas-arm-1b-left.stl, 2022-atlas-arm-1b-middle.iges, 2022-atlas-arm-1b-middle.stl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]
2022-03-31 Added drive mount. Added documentation for Brainsight mounting setup.
    [arm-L.iges, arm-L.stl, arm-angle.iges, arm-angle.stl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]
2022-03-31 Added drive mount spacer 'washers'.
    [drive-mount-washer-sw.stl, triad-washers.fcstd, washer-3up-1mm.iges, washer-3up-2mm.iges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]
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2022-03-31 Added 'obsolete' folder. Copied 'v2b' body and 'rod' models to 'close-long' drive.
    [arm-L.iges, arm-L.stl, arm-angle.iges, arm-angle.stl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]
2022-03-31 Added aux-probes and aux-cablings. Left most of the 'neuro2k' documents and models in 'neuro2k'.
    [2022-atlas-flange-mockup-8up.iges, 2022-atlas-flange-mockup-8up.stl, 2022-atlas-guide-tube-model.iges, 2022-atlas-probe-model-single.iges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]
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2022-04-01 Added clips directory.
    [2021-triad-short-close-jclip.iges, 2022-clip-compat-630.iges, clip-6p5-1up.iges, clip-6p5-2up.iges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]
2022-04-04 Added drawings for Shapeways Kevin-compatible clips.
    [tungsten-clip-sw-2021.fcstd]
2022-04-04 Initial candidate for a CNC-machinable 630 micron Kevin-compatible clip.
    [2022-clip-cnc-630-1up.iges, 2022-clip-cnc-630-1up.step, 2022-clip-cnc-630-1up.stl, 2022-clip-cnc-630-bottom.iges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]
2022-04-04 Moved rev 1 clip-cnc-630 files to obsolete folder.
    [2022-clip-cnc-630-1up.iges, 2022-clip-cnc-630-1up.step, 2022-clip-cnc-630-1up.stl, 2022-clip-cnc-630-bottom.iges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]
2022-04-04 Made a second revision of the CNC clip that hopefully meets Proto Labs' design rules.
    [2022-clip-cnc-630-r2-1up.iges, 2022-clip-cnc-630-r2-1up.step, 2022-clip-cnc-630-r2-bottom.iges, 2022-clip-cnc-630-r2-bottom.step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]
2022-04-06 Made a clip variant intended for use with Proto Labs metal printing process. Added CNC clip drawing.
    [2022-clip-3dp-360-1up.stl, 2022-clip-3dp-360-bottom.iges, 2022-clip-3dp-360-top.iges, 3dp-clips-2022.fcstd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]
2022-04-06 Updated DBC probe and board models.
    [2022-dbc-board-model-r1a.iges, 2022-dbc-board-model-r1b.iges, 2022-dbc-board-zc-model-r1a.iges, 2022-dbc-board-zc-model-r1b.iges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]
2022-04-06 Added DBC and ZC drawings.
    [probe-models-2022.fcstd]
2022-04-07 Moved DBC cable mount export files to short-reach drive folder.
    [cable-mount-dbc-20220322.iges, cable-mount-dbc-20220322.stl]
2022-04-07 Created skeletons of kevin, v2b, and v2c drive trees with IGES models. Still have to move CAD files and drawings over.
    [triad-kevin-arm-left.iges, triad-kevin-arm-middle.iges, triad-kevin-arm-right.iges, triad-kevin-motor.iges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]
2022-04-07 Interim version of the Atlas long-reach tools.
    [2022-atlas-probe-model-single.iges, atlas-jig-v2.fcstd, v2b-rod.iges]
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2022-04-08 Adjusted forceps tips. Mocked up vertical-rod cases for using forceps.
    [atlas-jig-v2.fcstd]
2022-04-12 Continued designing the Atlas long-reach jig.
    [atlas-jig-v2.fcstd, hflex-clip-fcwsf-29-19.iges]
2022-04-18 Updated DBC model with realistic flex and with desired handle.
    [2022-dbc-probe-model-r1c.iges, probe-models-2022.fcstd]
2022-04-20 Added DBC probes with 20mm handles. Added single-clamp close-spaced short-reach foot.
    [probe-models-2022.fcstd, triad-2mm-clamp-v2.fcstd]
2022-04-20 Initial revision of 3-piece close short-reach guide tube clamp.
    [triad-2mm-clamp-v2.fcstd]
2022-04-21 Fixed hole position on close short 3pc middle clamp. Added drawings of 3pc parts.
    [triad-2mm-clamp-v2.fcstd]
2022-04-21 Finished 1-piece and 3-piece low-profile drive feet for close-spaced short-reach. Finished mesh mockups of these with dbc probes.
    [2022-dbc-probe-model-r1c-20mm.iges, 20220421-close-short-1pc-assembly.iges, 20220421-close-short-1pc-clamp.iges, 20220421-close-short-1pc-clamp.stl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]
2022-04-21 Added STEP models of low-profile close-spaced short-reach drive feet.
    [20220421-close-short-1pc-clamp.step, 20220421-close-short-1pc-foot.step, 20220421-close-short-3pc-clamp-middle.step, 20220421-close-short-3pc-clamp-side.step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]
2022-04-21 Added board holder for loading DBC drives. Added discussion of variant guide tube clamps to README.
    [20220421-board-holder-dbc-angled.iges, 20220421-board-holder-dbc-angled.step, 20220421-board-holder-dbc-angled.stl, 20220421-board-holder-dbc-straight.iges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]
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2022-05-02 Added NeuroNexus probe loading jig (from neuro2k tree).
    [clip-rev2.iges, clip-rev2.stl, nn-guide-tube-jig-v2.fcstd, nn-v2-clip.stl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]
2022-05-03 Added 2019 chamber model example.
    [chamber-20190111-fus-m1.stl]
2022-05-03 Added meshes and README for Kevin drives.
    [drive-body-new-sw-v2.stl, drive-body-new-sw.stl, drive-body-new.stl, drive-body-old-sw-v2.stl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]
2022-05-03 Moved old v2b/v2c STL meshes into tree.
    [cmount-v2b1.stl, cmount-v2c5-mirrored.stl, cmount-v2c5.stl, nn-v2b-foot-block-left-csink.stl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]
2022-05-03 Moved old NeuroNexus probe STL models into tree.
    [2019-nn-probe-model-hollow.stl, 2019-nn-probe-model-solid.stl]
2022-05-03 Moved 3d printed NeuroNexus mockup flanges into tree.
    [2019-nnex-flange-mockup-set.stl]
2022-05-03 Moved Triad drive arm reference to here, as it was taken from this drive's models.
    [triad-arms-ref-202203.fcstd]
2022-05-04 Copied probe models from 'v2b' CAD file into tree.
    [probe-models-2020.fcstd]
2022-05-04 Added Kevin drive models from 'v2b' CAD file.
    [drive-model-kevin.fcstd]
2022-05-04 Copied Atlas thin flex model from 'v2b' CAD file.
    [atlas-flex-2020.fcstd]
2022-05-04 Copied heavy flex cable mount CAD models to their own folder. Added drawings.
    [cmount-v2b1.stl, cmount-v2c5-mirrored.stl, cmount-v2c5.stl, cmounts-hflex.fcstd]
2022-05-05 Added Isaac's tungsten-clip arms for v2b and v2c drives.
    [triad-tungsten-v2b-left.iges, triad-tungsten-v2b-left.step, triad-tungsten-v2b-middle.iges, triad-tungsten-v2b-middle.step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]
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2022-05-06 Added interim CAD files for physical mockup proxies of drives.
    [2021-triad-short-close-foot.iges, 20220322-dbc-model-drive-empty.stl, 20220329-nn-model-empty.stl, 20220421-close-short-1pc-assembly.iges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]
2022-05-16 Milestone for the close short-reach drive proxies. Added renders.
    [proxy-templates.fcstd]
2022-05-17 Added DBC board plus ZC narrow template. Added close short proxy meshes.
    [proxy-dbc-zif-narrow.stl, proxy-drive-close-short.stl, proxy-template-close-short-1pc.stl, proxy-template-close-short-2lv.stl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]
2022-05-17 Moved clip meshes and models to appropriate subdirectories. Started Atlas drive tungsten variant.
    [2022-clip-3dp-630-1up.stl, 2022-clip-3dp-630-bottom.iges, 2022-clip-3dp-630-top.iges, 2022-clip-cnc-630-r2-1up.iges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]
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2022-05-18 Finished tungsten arms for atlas-configured long-reach drive, with tight clearances for printing.
    [triad-long-atlas.fcstd]
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2022-05-18 Made tungsten arm drawing, for clearance references.
    [triad-long-atlas.fcstd]
2022-05-18 Started close-spaced long-reach DBC with closer pattern. Made drawings of close-spaced short-reach 2-level foot.
    [2021-triad-short-close-foot.iges, 2021-triad-short-close-jclip.iges, 2022-dbc-guide-tube-model.iges, clip-6p5-1up.iges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]
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2022-05-20 Fixed inset depth note on long-reach Atlas tungsten arm drawing.
    [triad-long-atlas.fcstd]
2022-05-20 Exported IGES and STL models for v2 close-spaced short-reach arms.
    [20220520-close-short-arm-left-medium.iges, 20220520-close-short-arm-left-medium.stl, 20220520-close-short-arm-left-narrow.iges, 20220520-close-short-arm-left-n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]
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2022-05-26 Added IGES models of close-spaced short-reach mockups.
    [20220526-model-dbc-1pc-loaded.iges, 20220526-model-dbc-2lev-loaded.iges, 20220526-model-dbc-3pc-loaded.iges, 20220526-model-nn-2lev-loaded.iges]
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2022-06-28 Modified proxy bodies for tighter post clearance and less wobble.
    [proxy-templates.fcstd]
2022-06-28 Added 1mm more clearance for the mounting arm. This does not match the real drives' geometry but should guarantee clearance.
    [proxy-templates.fcstd]
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2022-06-29 Modified DBC cable mount for correct mounting dimensions.
    [20220523-cable-mount-dbc-medium.iges, 20220523-cable-mount-dbc-medium.stl, 20220523-cable-mount-dbc-narrow.stl, 20220523-cable-mount-dbc-wide.stl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]
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2022-06-29 Adjusted clearances on heavy flex mounts and updated FreeCAD file to use 1.19 conventions.
    [cmounts-hflex.fcstd]
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
